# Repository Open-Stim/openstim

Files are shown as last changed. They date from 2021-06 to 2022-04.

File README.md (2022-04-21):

# <P align="center"> OPEN-STIM - OPEN SOURCE HARDWARE ARDUINO BASED ELECTRICAL STIMULATOR 
<table align='center'>
<tr align='center'>
<td align='center'>

Licence | OSHWA |
:-------------------------:|:-------------------------:|
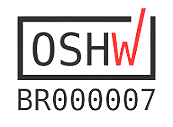
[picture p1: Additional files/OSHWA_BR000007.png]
(https://certification.oshwa.org/br000007.html)
 |  

</table> 
 
## <P align="center"> FEDERAL UNIVERSITY OF SÃO JOÃO DEL-REI – UFSJ
### <P align="center"> NEUROENGINEERING AND NEUROSCIENCE INTERDISCIPLINARY LABORATORY – LINNCE
&emsp; &emsp; &emsp; &emsp; &emsp; &emsp; &emsp; &emsp; &emsp; &emsp; &emsp; &emsp; &emsp;UFSJ &emsp; &emsp; &emsp; &emsp; LINNCE

### DEVELOPED BY:
Maikon Lorran Santos - maikon.lorran@hotmail.com <br/>
João Daniel Nolasco - joaodani@hotmail.com <br/>
Vinícius Rosa Cota: - vrcota@ufsj.edu.br <br/>

### PROJECT'S GOAL
<P align="justify"> The main objective of the project was to develop and build a low-cost electrical stimulator for experimental stimulation electrophysiology
based on the Arduino platform, maximizing ease of use, versatility, and openness. The idea was to develop an output stage shield capable of 
delivering mono or biphasic pulses with constant current (even in face of varying output impedances) easily attachable to an Arduino microcontroller
board. Stimulation parameters (pulse frequency, pulse duration, number and polarity of phases) can be controlled by a touch screen and/or by knobs.
In this entry, we published the version which is controlled mostly by a touch screen display, but this can be easily substituted by manual controls 
(switches and additional knobs) with or without a LCD display to further reduce costs (variation not yet published). These variations and openness of 
the design (which is provisionally certified by OSHWA with UID BR000007) makes Open Stim a very flexible stimulation platform for experienced users and, 
at the same time, also a ready-to-use device for researchers not skilled on electronics. 

### DISCLAIMER
<P align="justify"> We offer this design as is and although it has been successfully tested with care and to the best of our knowledge, we do not provide any 
 warranty in any aspect.

### STIMULATOR PARAMETERS
-Current: 15 µA up to 1200 µA <br/>
-Frequency: 0.1 Hz up to 300 Hz <br/>
-Duty Cycle: 4 µs up to 1 s <br/>
-Biphasic Pulses <br/>
-Low battery indicator <br/>

### OPEN STIM

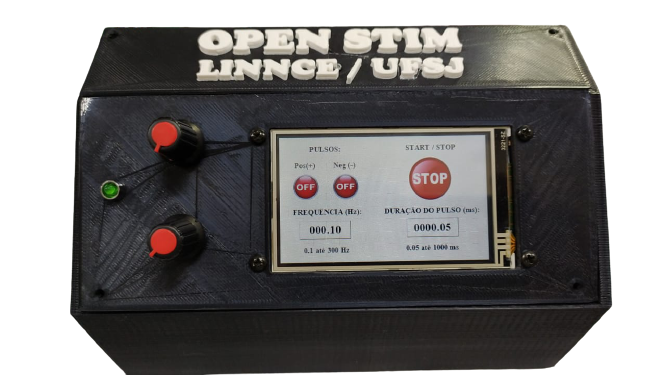
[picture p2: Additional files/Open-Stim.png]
OPEN-STIM

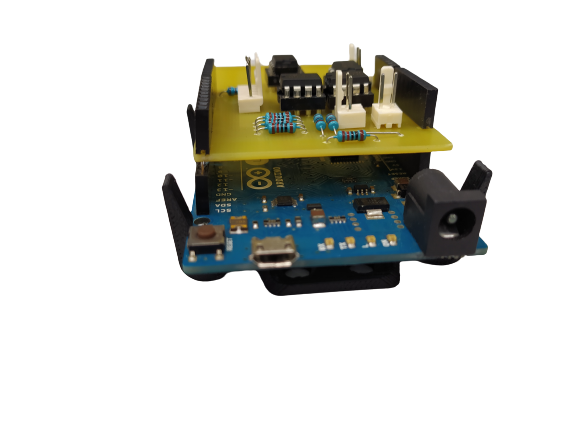
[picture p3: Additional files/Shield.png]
Shield
&emsp; &emsp; &emsp; 
### • More about the lab, at our website: [LINNce](https://ufsj.edu.br/vrcota/linnce.php)

### LICENSE
##### Documentation licensed under the Creative Commons Attribution Share Alike 4.0 International License

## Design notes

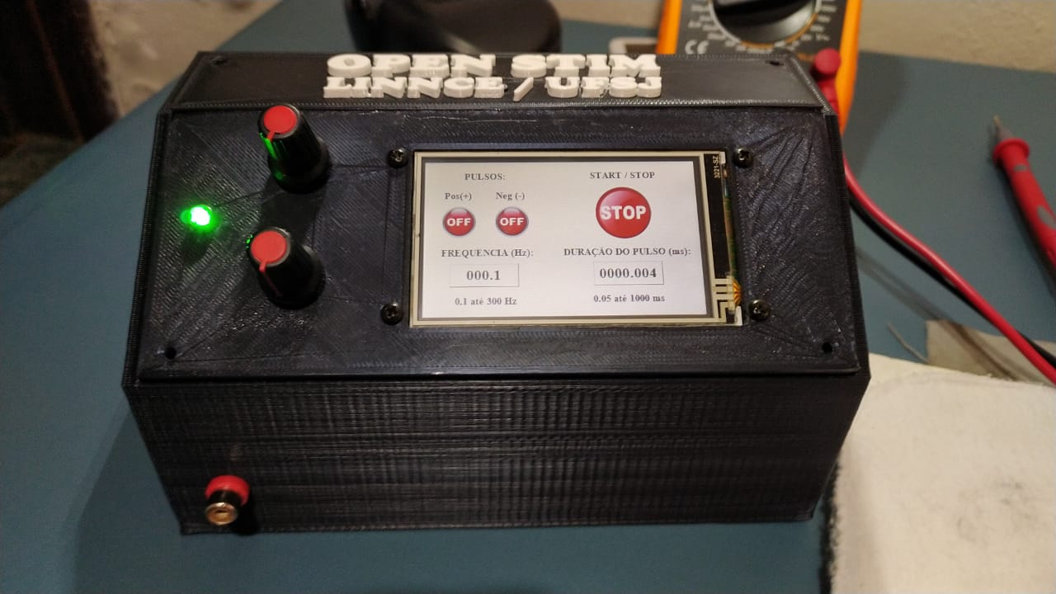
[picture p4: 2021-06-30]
Photos/Box/IMG-20210409-WA0050.jpg

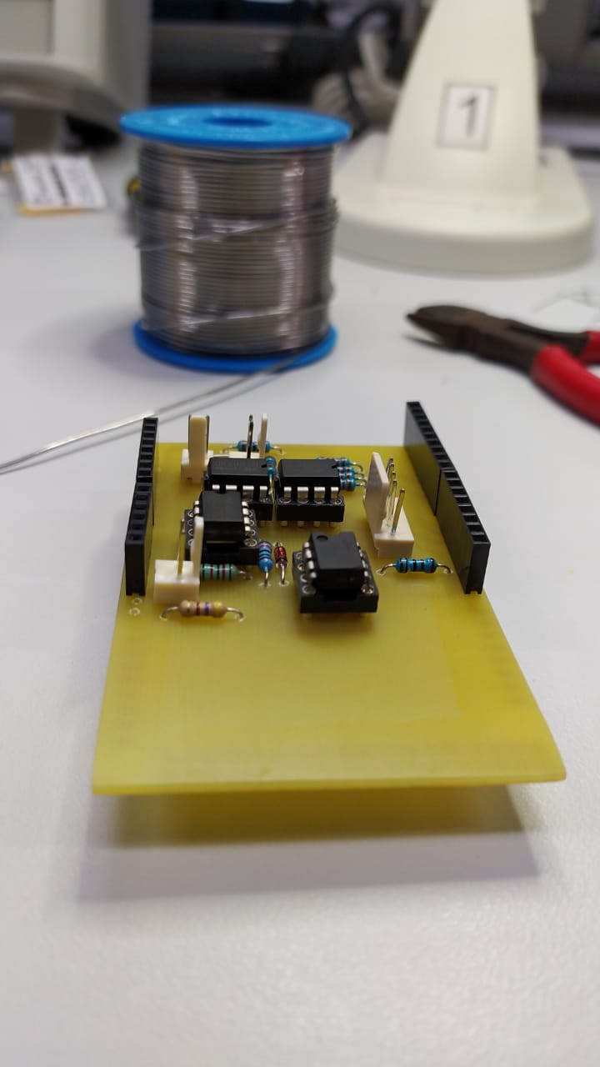
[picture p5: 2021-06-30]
Photos/PCB/Shield/IMG-20210302-WA0013.jpg

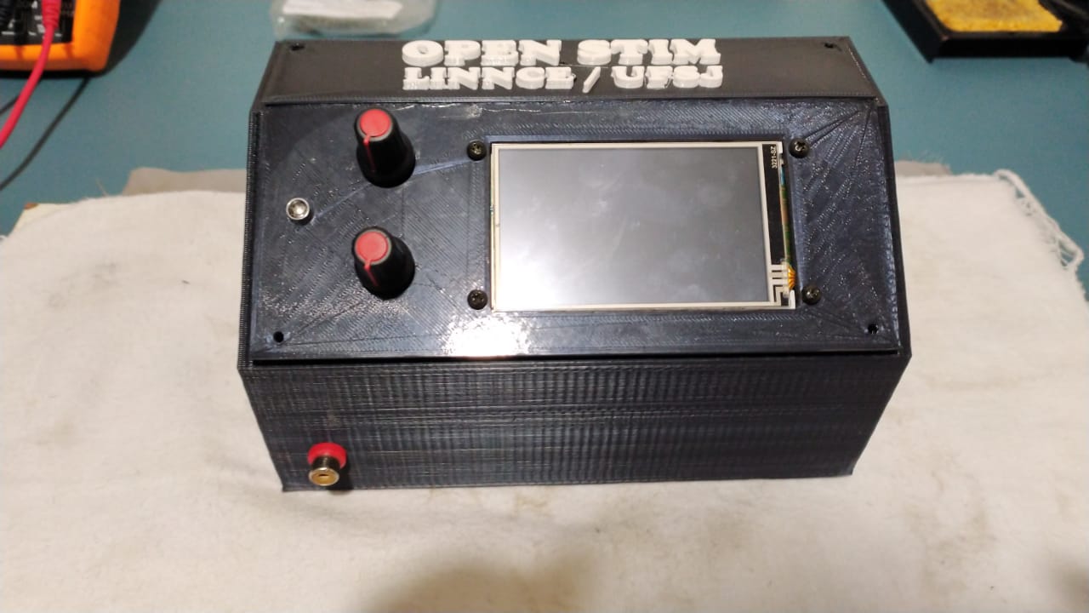
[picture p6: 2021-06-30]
Photos/Box/IMG-20210409-WA0058.jpg

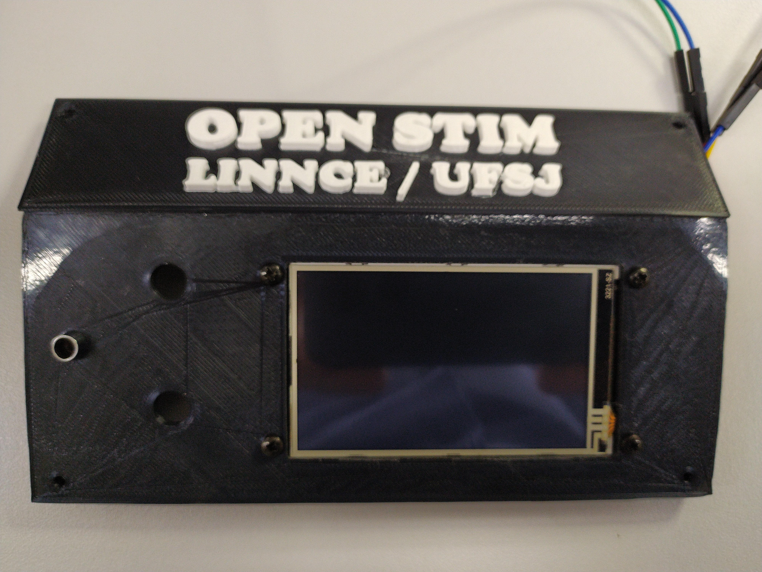
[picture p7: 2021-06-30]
Photos/Box/IMG_20210328_171714_BURST1.jpg

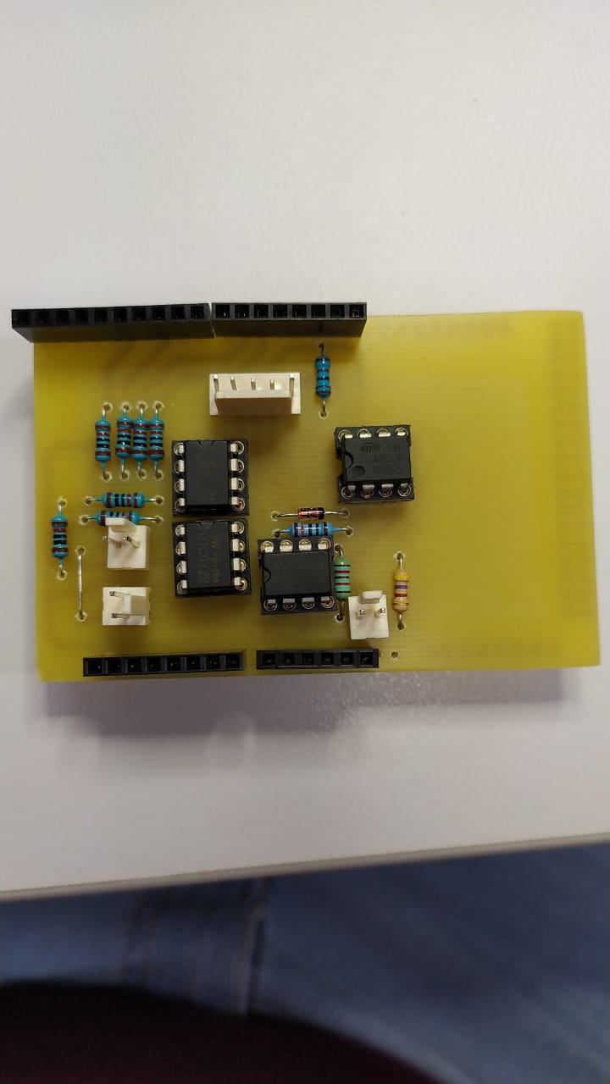
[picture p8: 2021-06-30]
Photos/PCB/Shield/IMG-20210302-WA0009.jpg

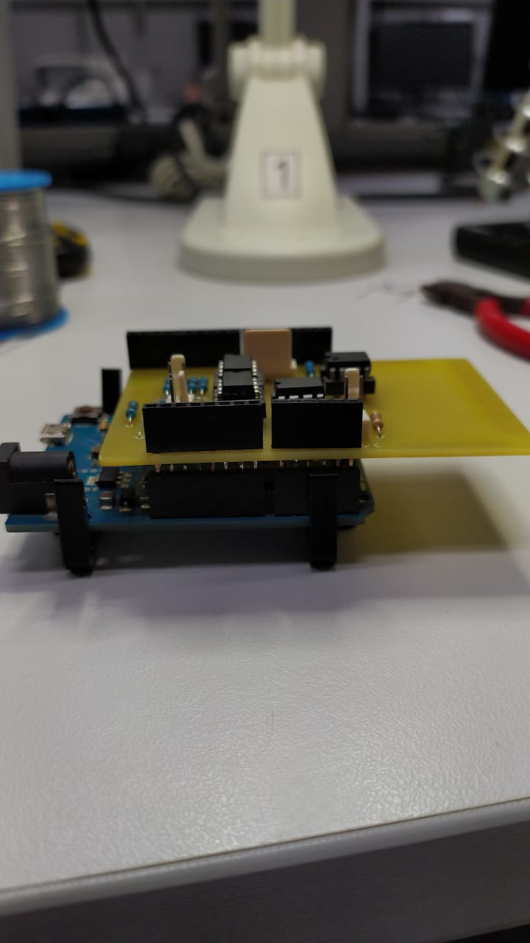
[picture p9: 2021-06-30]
Photos/PCB/Shield/IMG-20210302-WA0015.jpg

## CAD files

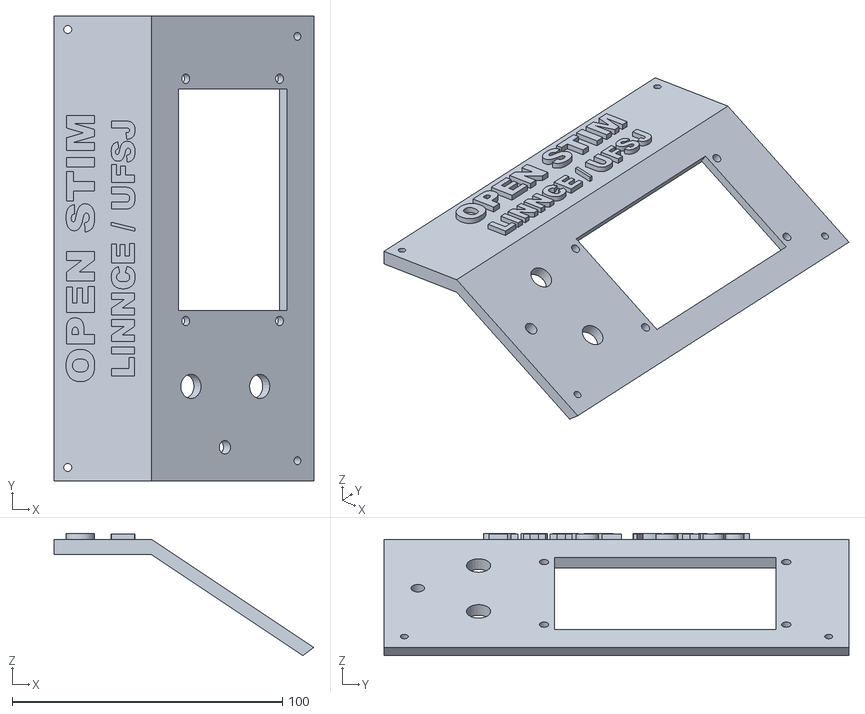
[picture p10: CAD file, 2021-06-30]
3D printing/SketchUp/STL print/Print_Cover.stl
96.0 x 172.0 x 45.2

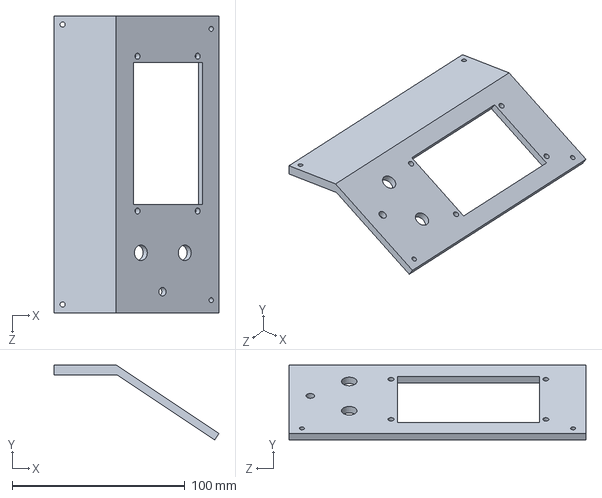
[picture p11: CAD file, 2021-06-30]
3D printing/SolidWorks/tampa.SLDPRT
95.5 x 43.4 x 171.8 mm

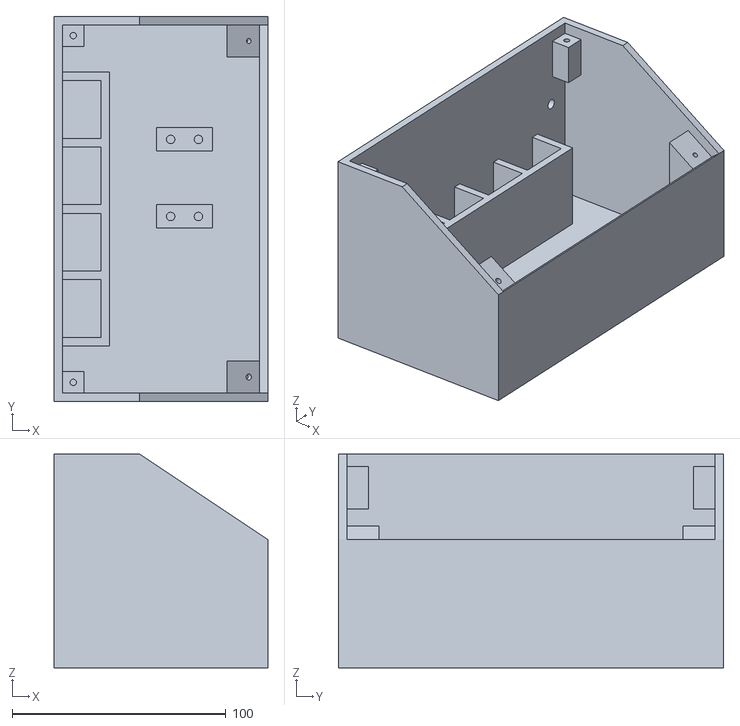
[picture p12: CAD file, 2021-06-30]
3D printing/SketchUp/STL print/Print_Box.stl
100.0 x 180.0 x 100.0

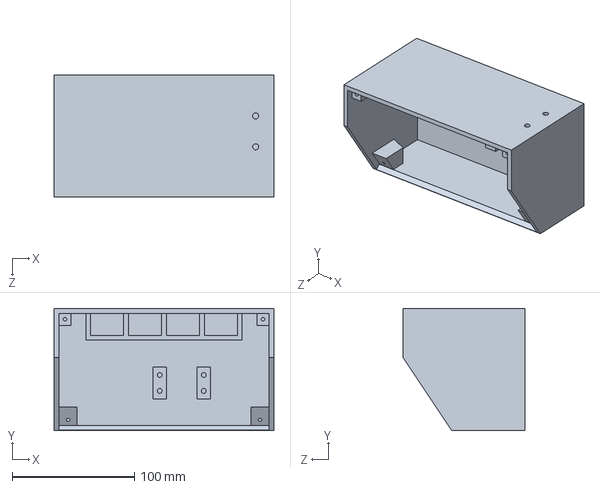
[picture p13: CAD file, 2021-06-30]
3D printing/SolidWorks/caixa.SLDPRT
180.0 x 100.0 x 100.0 mm

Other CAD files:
3D printing/SketchUp/Box Print/Box.skp
3D printing/SketchUp/Cover print/Cover.skp
3D printing/SolidWorks/caixa.IGS
3D printing/SolidWorks/tampa.IGS

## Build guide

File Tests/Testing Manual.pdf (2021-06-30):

OPEN STIM - ELECTRICAL STIMULATOR OPEN SOURCE HARDWARE

## FEDERAL UNIVERSITY OF SÃO JOÃO DEL-REI – UFSJ

NEUROENGINEERING AND NEUROSCIENCE INTERDISCIPLINARY LABORATORY – LINNCE

# OPEN STIM ELECTRICAL TESTING MANUAL

Brazil, May 2021

## OPEN STIM ELECTRICAL TESTING MANUAL

¹ FEDERAL UNIVERSITY OF SÃO JOÃO DEL-REI – UFSJ

² LABORATORY OF NEUROENGINEERING AND NEUROSCIENCE– LINNCE

DEVELOPED BY:

¹ ² Maikon Lorran Santos - maikon.lorran@hotmail.com

¹ João Daniel Nolasco - joaodani@hotmail.com

¹ ² Vinícius Rosa Cota: - vrcota@ufsj.edu.br

Address: Frei Orlando Square, 170, Center – São João del-Rei – Minas Gerais - Brazil

Brazil, May 2021

This manual will assist in testing Open

Stim. They are electrical tests, to be

carried out on bench with oscilloscope

and multimeter. It is possible to check the

frequency, the stimulation current, pulse

duration, pulse phase, slew rate, among

others.

## SUMMARY

3 | P á g i n a

# CHAPTER 1

## INTRODUCTION AND OBJECTIVES

The tests are of fundamental importance to verify all the functionalities and limitations

of the hardware and software. As it is a prototype, we do not have any tests performed on

animals yet. Thus, all the tests were carried out in an electronics laboratory, simulating the brain

or tissue with electrical resistors.

These tests enable us to verify that the configured parameters are actually being

delivered by the stimulator. In addition, we want to know the percentage of error contained in

each parameter, to establish its acceptable margins, and to find limitations. After all the tests

are done and results are consolidated and that the values found meet the need for your

research, there is the possibility of tests on animals. Bear in mind that, for tests on animals,

approval from the institution's ethics committee is required before starting any experimental

procedure.

The main purpose of this manual is explain how to check the frequency, pulse duration,

pulse phase, electrical current and slew rate being delivered by the stimulator.

# CHAPTER 2

## TESTING EQUIPMENT

To test Open Stim, we used the Agilent oscilloscope model DSO-X 2002A, which is shown

in Figure 1. However, any oscilloscope with basic functions is capable of carrying out the

necessary tests.

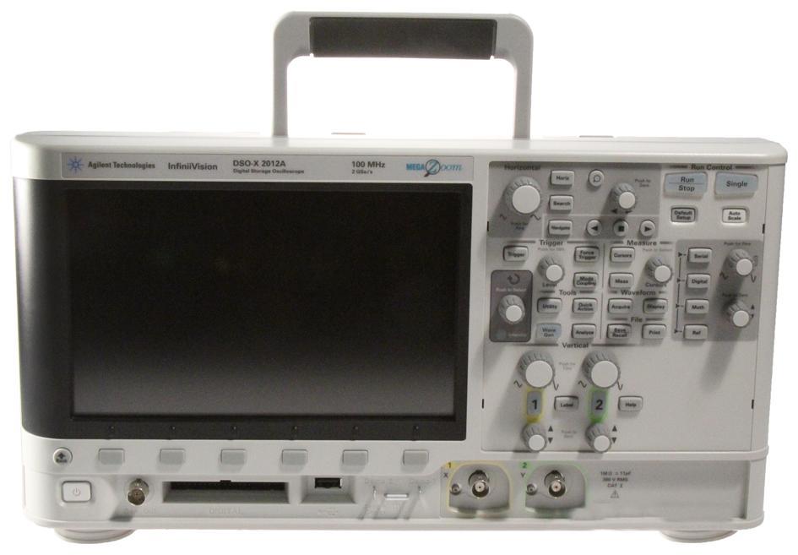
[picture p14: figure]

Figure 1 - Agilent DSO-X 2002A Oscilloscope

The multimeter used was the Agilent model U1241B, which is in Figure 2. It is important

that the multimeter is capable of measuring microamperes and has good accuracy, since the

stimulator supplies very low output currents. Before starting to measure the currents, check the

maximum current that the multimeter can measure, and also check that the low current fuse is

not open.

Another question that is a common mistake is the multimeter's probes. Check if they

are connected to the multimeter for current measurement. Also confirm the current scale to be

used, which is direct current in microamperes.

Finally, check the batteries of the multimeter, as it will be used for a long period of time.

Remove and measure all and, if necessary, replace them.

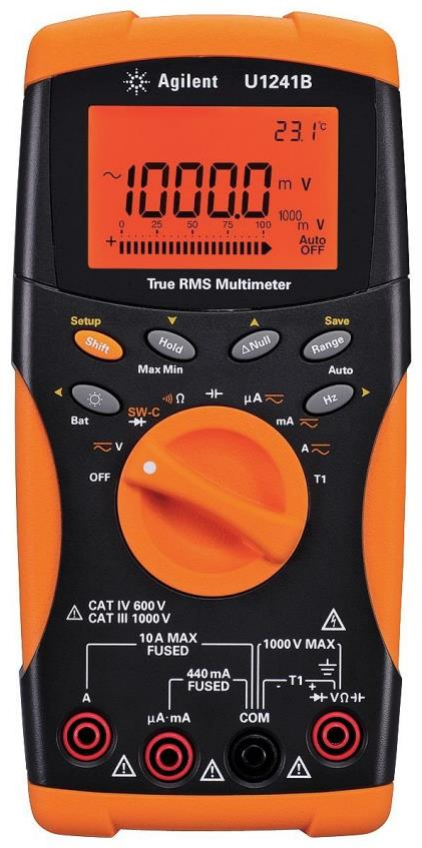
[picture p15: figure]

Figure 2 - Agilent U1241B Multimeter

We also recommend having on the bench some cables for jumpers, alligator claws,

cutting pliers, stripper pliers, electrical tape, note paper, pen, calculator, in short, everything

that will facilitate the quality of the tests.

# CHAPTER 3

## FREQUENCY TEST

To check the accuracy of the frequency, only the oscilloscope is needed. Consider 5 %

error for the frequency, this value meets the requirements of the project.

To carry out this test, put a resistance on the output, between 1K and 10K that will

simulate the brain of the animal. Place the ends of the oscilloscope in this output resistor. Now

turn on the stimulator, enter frequency values between 0.1 Hz and 300 Hz by typing the value

on to the Nextion screen. Of course, also entering the pulse width values is required, but at this

moment, we will not be checking this parameter, only the frequency. Enter large values of pulse

width, such as 50% of the duty cycle (period between firing of pulses), to facilitate viewing on the oscilloscope screen. For example: for a frequency of 20 Hz, the largest pulse width is 50 ms

However, as they are biphasic pulses, we have 25 ms for each pulse. Therefore, an average value

to be entered for pulse width for the frequency of 20 Hz would be 12.5 ms. Table 1 contains the

frequency results measured and the margin of error found for each value.

Table 1 - Frequency

If the frequencies are not within the expected levels, check the connections in order to

reduce or eliminate noise. Another point is to check the Arduino code, in case the difference is

very large, obtaining an error greater than 5%. Below are some screenshots of the oscilloscope,

showing the values found in the Open Stim built at UFSJ, by LINNCE.

FREQUENCY (Hz)

MEASURED

FREQUENCY (Hz)

ERROR (%)

300 | 299.19 | 0.27
250 | 249.60 | 0.16
200 | 199.63 | 0.18
150 | 149.78 | 0.15
100 | 99.95 | 0.05
90 | 89.92 | 0.09
80 | 79.85 | 0.19
70 | 69.86 | 0.20
60 | 59.84 | 0.26
50 | 49.93 | 0.14
40 | 39.99 | 0.02
30 | 29.96 | 0.13
20 | 19.94 | 0.30
15 | 14.96 | 0.27
10 | 9.99 | 0.1
9 | 8.99 | 0.11
8 | 7.99 | 0.12
7 | 6.98 | 0.29
6 | 5.99 | 0.17
5 | 4.99 | 0.20
4 | 3.99 | 0.25
3 | 2.99 | 0.33
2 | 1.99 | 0.50
1 | 0.99 | 1.0
0.5 | 0.48 | 4.17

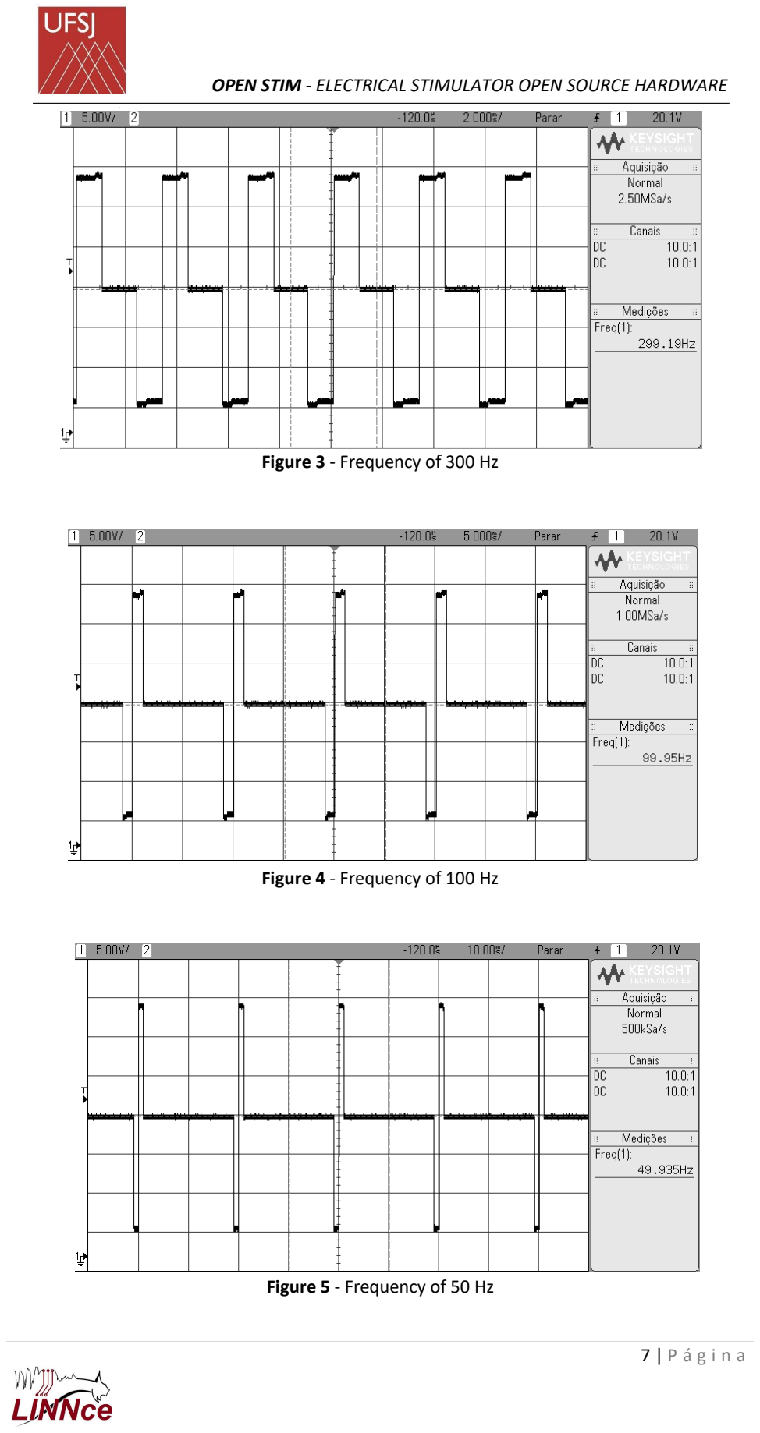
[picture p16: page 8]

Figure 3 - Frequency of 300 Hz

Figure 4 - Frequency of 100 Hz

Figure 5 - Frequency of 50 Hz

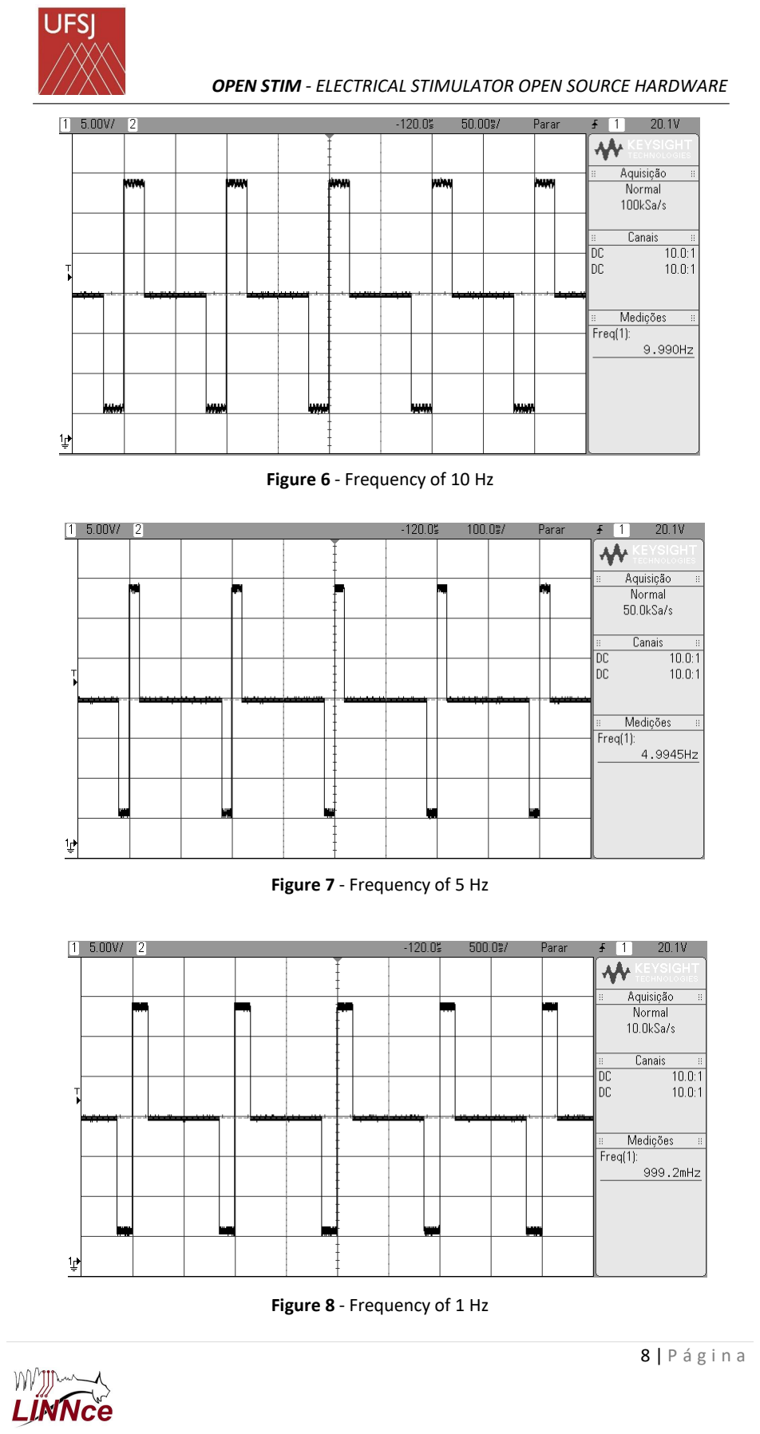
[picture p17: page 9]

Figure 6 - Frequency of 10 Hz

Figure 7 - Frequency of 5 Hz

Figure 8 - Frequency of 1 Hz

# CHAPTER 4

## PULSE WIDTH TEST

The pulse width test follows the same reasoning as the frequency test: enter the value

on the Nextion screen and check the value on the output with the oscilloscope and considering

a margin of error of 5 %. Table 2 shows some results found.

Table 2 - Pulse Width

The following screenshots show the values mentioned above. The values are found with

the aid of the oscilloscope cursor tool, over the X.

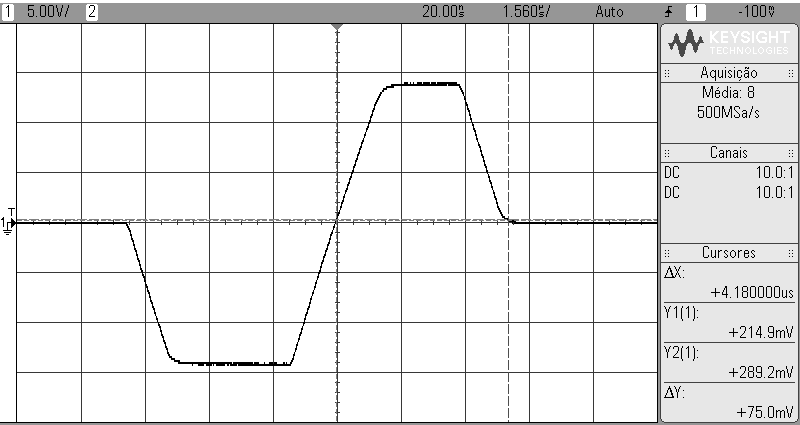
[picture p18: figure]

Figure 9 - Positive Pulse Width 4 µs

PULSE WIDTH (ms)

MEASURED POSITIVE

PULSE WIDTH (ms)

ERROR (%)

MEASURED NEGATIVE

PULSE WIDTH (ms)

ERROR (%)

4 µs (@280 Hz) | 4.18 µs | 4.31 % | 5.08 µs | 21.26 %
64 µs (@20Hz) | 64 µs | 0 % | 65.2 µs | 1.84 %
500 µs (@2 Hz) | 514 µs | 2.72 % | 514 µs | 2.72 %

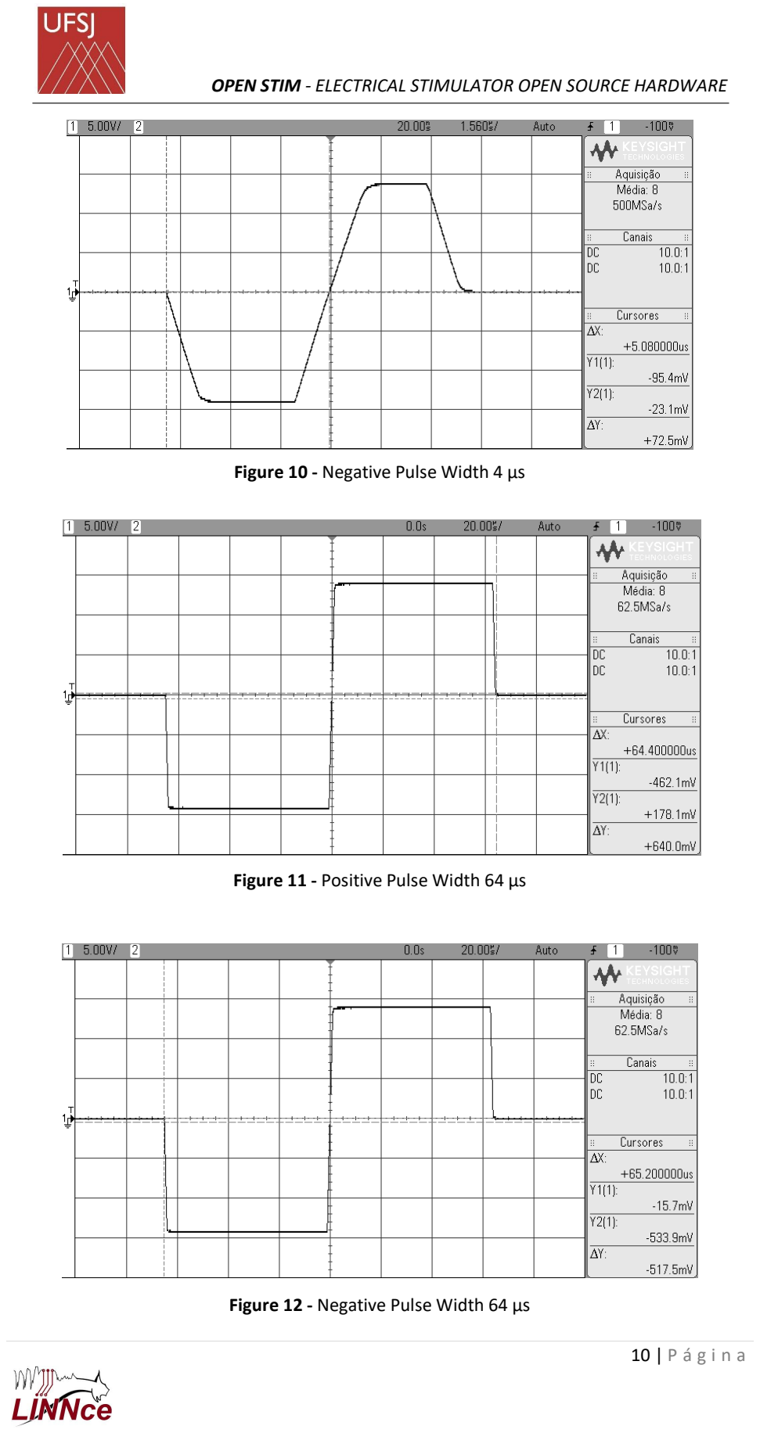
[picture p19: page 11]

Figure 10 - Negative Pulse Width 4 µs

Figure 11 - Positive Pulse Width 64 µs

Figure 12 - Negative Pulse Width 64 µs

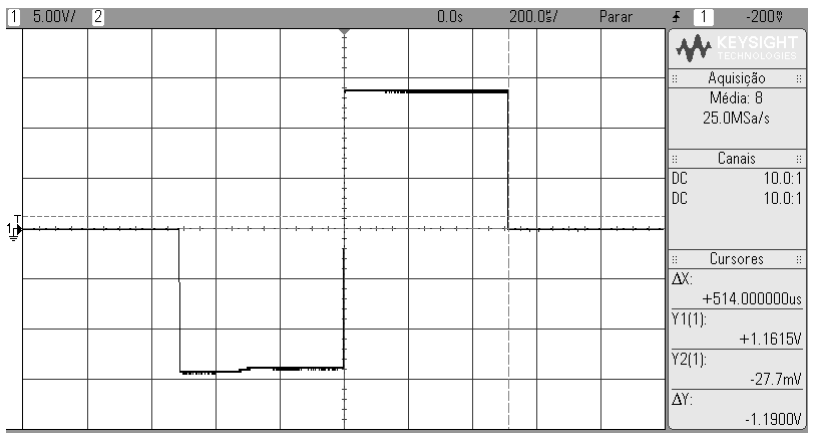
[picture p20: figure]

Figure 13- Positive Pulse Width 500 µs

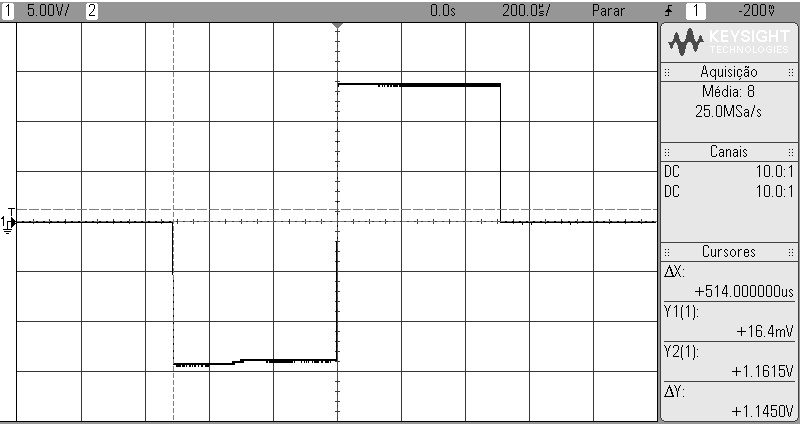
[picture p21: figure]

Figure 14 - Negative Pulse Width 500 µs

4.1 – PULSE WIDTH vs. FREQUENCY

As described in the Open Stim manual, the device is operated by means of PWM.

Thus, it depends solely on the 16 MHz internal clock of Atmega 32u4 processor. In this

sense, it is important to understand PWM operation and configuration in this processor

to fully grasp the link between these two parameters (pulse width and frequency), how

they interfere with each other, and what is the limitation of such form of operation.

When lower frequencies are desired, the frequency of the internal clock can be

divided by factors expressed as powers of base 2 (2N
) using the prescaler function (see

chapter 15 of the ATMEGA 32u4 datasheet). For instance, setting the prescaler to 1 yields the original frequency, that is, 16 MHz. When the prescaler is 2, we get 8 MHz,

and so on. Now, to obtain frequency values between the original frequency and its by-2

divisions, it is necessary to count a fixed quantity of clock pulses. This is done by the

internal Atmega 32u4 10-bit counter. Thus, for instance, if we use a prescaler of 64 and

a count of 1024 pulse, we obtain a frequency of 244.14 Hz.

250x10³
1024 = 244.14 Hz

Using the same prescaler, but counting 833 pulses instead, we get 300.12 Hz.

Table 3 below shows, according to the prescaler chosen, the new (divided) base

frequency, the minimum possible frequency (when 1024 pulses are counted), and the

maximum value of frequency used in this project (which is the minimum of the next

prescaler). We only show prescaler values used in our programming.

Configuration of pulse duration uses exactly the same clock system, including the

prescaler and the 10-bit counter. That means widths are limited to multiples of the pulse

duration of the divided clock signal. For instance, by using a prescaler value of 64, which

yields a divided frequency of 250 KHz, the minimum duration of a pulse will be 1/250000

Hz = 4 ms, which is shorter than most experimental applications in neuroscience. On the

other hand, if slower firing frequencies are desired, only longer pulse durations will be

available. For instance, if a prescaler of 16384 is used, the base frequency becomes

976,5625 Hz. In this case, the lowest frequency is circa 0.95 Hz with the shortest pulse

duration of 1.024 ms. Table 4 shows minimum pulse width obtainable for each prescaler.

In our experience, the range of values made available by this technology is

sufficient for a very wide range of experimental protocols used in neuroscience and also

in other areas of physiology (e.g., muscular and cardiac). If needed, one should consider

developing of a derivative of Open Stim using Arduino boards with better performance.

For instance, Arduino Due has an internal counter of 32 bits which will greatly improve

the granularity of pulse widths and frequency ranges. It is important to highlight, though,

that Arduino Due is not readily interchangeable with Leonardo, given, among other

technical aspects, differences in operation voltages (3.3 V vs. 5 V).

(1)

Table 3 - Frequency limits

Table 4 - Limit of pulse width by frequency range

For frequencies below 0.95 Hz, it is necessary to use the Arduino delay function and it is

no longer possible to do it directly using PWM. Using the delay function, the processor halts the

execution of the program until the commanded time has passed, which causes system

unresponsiveness. That is why such approach was avoided and used only when absolutely

necessary (frequencies below 0.95 Hz). Users and builders should bear this in mind when using

Open Stim or creating its derivatives.

PRESCALER | NEW FREQUENCY (Hz) | MINIMUM FREQUENCY (Hz) | MAXIMUM FREQUENCY (Hz)
64 | 250000 | 244.14 | 488.28
128 | 125000 | 122.07 | 244.14
256 | 62500 | 61.03 | 122.07
512 | 31250 | 30.52 | 61.03
1024 | 15625 | 15.26 | 30.52
2048 | 7812.5 | 7.63 | 15.26
4096 | 3906.25 | 3.81 | 7.63
8192 | 1953.125 | 1.91 | 3.81
16384 | 976.5625 | 0.95 | 1.91

PRESCALER

MINIMUM

FREQUENCY (Hz)

MAXIMUM

FREQUENCY (Hz)

MINIMUM PULSE

WIDTH (ms)

64 | 244.14 | 488.28 | 0.004
128 | 122.07 | 244.14 | 0.008
256 | 61.03 | 122.07 | 0.016
512 | 30.52 | 61.03 | 0.032
1024 | 15.26 | 30.52 | 0.064
2048 | 7.63 | 15.26 | 0.128
4096 | 3.81 | 7.63 | 0.256
8192 | 1.91 | 3.81 | 0.512
16384 | 0.95 | 1.91 | 1.024

# CHAPTER 5

## CONSTANT CURRENT TEST

The constant current test consists in verifying that output current stays the same

even if the output impedance changes, for instance, when performing stimulation to

different animals. Although simplistically, we can approximate the equivalent resistance

of Wistar rats’ brains to a range between 1 kΩ and 10 KΩ on average. Thus, we

performed the tests considering values between 1 KΩ and 10 KΩ, which were

represented by a resistor connected to the stimulator output.

With the multimeter connected in series with the output resistance and on the

direct current scale, proceed as follows:

1) Define the first value of output resistor with the first possible value being 1 KΩ and

the last possible value being 10 KΩ.

2) Define the resistor of the resistor board, that is, R10, the first possible value being

4.02 KΩ and the last 360 KΩ.

3) We suggest that you start as follows: Set the output resistance to 10 KΩ, which is the

maximum value, and vary R10 from 4.02 KΩ to 360 KΩ using the rotary switches. In this

way, all currents for output equal to 10 KΩ are measured. Note the positive and negative

current values. In order to obtain the correct current and not the average RMS, set a low

frequency with a large pulse width. In this way, the multimeter is able to make the

correct measurement. If you prefer, it is also possible to do it by assessing the voltage in

the output resistor and using Ohm's law relation to obtain the current.

4) After taking the measurements for R11 equal to 10 KΩ, change the resistance to a

lower one, in this work we use the following values: 1 KΩ, 2 KΩ, 4.02 KΩ, 6.12 KΩ, 7.15

KΩ, 8.25 KΩ and 10 KΩ. Follow in the same way as mentioned above and measure the

positive and negative currents to the value of 8.25 KΩ, for example. Then to 7.15 KΩ,

6.12 KΩ, 4.02 KΩ, 2 KΩ, 1 KΩ.

5) Now with all measured currents, calculate the error between the maximum and

minimum positive current and then the error between the maximum and minimum

negative current. This error cannot exceed 10%.

Table 5 and Table 6 show the positive and negative currents, respectively, with

the values found by the authors of the project, as well as their error.

Table 5 - Positive current measurement

R10 (KΩ) | 1 KΩ | 2 KΩ | 4,02 KΩ | 6,19 KΩ | 7,15 KΩ | 8,25 KΩ | 10 KΩ | ERROR
4,02 | 1252 | 1250 | 1247 | 1245 | 1244 | 1240 | 1239 | 1,04%
4,7 | 1068 | 1065 | 1064 | 1062 | 1061 | 1058 | 1050 | 1,69%
5,6 | 902 | 900 | 896 | 894 | 892 | 890 | 885 | 1,88%
6,19 | 810 | 806 | 805 | 804 | 803 | 800 | 795 | 1,85%
7,15 | 702 | 700 | 697 | 695 | 694 | 692 | 686 | 2,28%
8,25 | 609 | 606 | 605 | 604 | 604 | 600 | 595 | 2,30%
10 | 505 | 502 | 500 | 500 | 498 | 495 | 491 | 2,77%
12,1 | 415 | 414 | 413 | 413 | 411 | 405 | 400 | 3,61%
14 | 360 | 357 | 355 | 355 | 354 | 350 | 347 | 3,61%
16,9 | 302 | 300 | 298 | 295 | 294 | 291 | 288 | 4,64%
20,5 | 250 | 248 | 245 | 243 | 243 | 241 | 240 | 4,00%
24,9 | 208 | 206 | 205 | 202 | 199 | 197 | 195 | 6,25%
33,2 | 154 | 153 | 153 | 152 | 150 | 149 | 148 | 3,90%
44,2 | 115 | 114 | 112 | 110 | 111 | 110 | 108 | 6,09%
56,2 | 92 | 91 | 90 | 90 | 88 | 88 | 86 | 6,52%
61,9 | 83 | 83 | 82 | 81 | 80 | 79 | 77 | 7,23%
71,5 | 72 | 71 | 70 | 70 | 69 | 68 | 67 | 6,94%
78,7 | 64 | 64 | 63 | 63 | 62 | 62 | 61 | 4,69%
100 | 51 | 51 | 50 | 50 | 49 | 47 | 47 | 7,84%
120 | 43 | 42 | 42 | 41 | 41 | 40 | 39 | 9,30%
150 | 34 | 34 | 33 | 33 | 33 | 33 | 32 | 5,88%
240 | 22 | 22 | 22 | 21 | 21 | 21 | 20 | 9,09%
360 | 15 | 15 | 15 | 14 | 14 | 14 | 14 | 6,67%

Table 6 - Negative current measurement

# CHAPTER 6

## SLEW RATE

The Slew Rate is the rate of change of the output voltage over time, according to equation 6, with its unit of measurement V / µs.

SR =

dV0
dt

The slew rate of Open Stim is limited to the properties of the operational

amplifier, which cannot change its output voltage instantly when there is a change in

R10 (KΩ) | 1 KΩ | 2 KΩ | 4,02 KΩ | 6,19 KΩ | 7,15 KΩ | 8,25 KΩ | 10 KΩ | ERROR
4,02 | 1245 | 1241 | 1239 | 1238 | 1238 | 1238 | 1235 | 0,80%
4,7 | 1059 | 1059 | 1057 | 1055 | 1055 | 1054 | 1048 | 1,04%
5,6 | 897 | 895 | 892 | 890 | 890 | 888 | 885 | 1,34%
6,19 | 807 | 805 | 803 | 802 | 800 | 799 | 795 | 1,49%
7,15 | 695 | 694 | 692 | 691 | 690 | 687 | 685 | 1,44%
8,25 | 605 | 604 | 603 | 602 | 601 | 599 | 596 | 1,49%
10 | 500 | 498 | 496 | 495 | 495 | 493 | 490 | 2,00%
12,1 | 413 | 411 | 410 | 408 | 408 | 405 | 400 | 3,15%
14 | 357 | 355 | 354 | 353 | 352 | 350 | 345 | 3,36%
16,9 | 300 | 297 | 295 | 293 | 292 | 291 | 290 | 3,33%
20,5 | 247 | 245 | 244 | 242 | 242 | 240 | 238 | 3,64%
24,9 | 205 | 202 | 200 | 199 | 198 | 197 | 195 | 4,88%
33,2 | 152 | 150 | 149 | 149 | 149 | 147 | 145 | 4,61%
44,2 | 115 | 114 | 112 | 112 | 111 | 110 | 108 | 6,09%
56,2 | 91 | 91 | 90 | 88 | 87 | 87 | 85 | 6,59%
61,9 | 82 | 81 | 80 | 80 | 79 | 79 | 77 | 6,10%
71,5 | 72 | 71 | 70 | 70 | 69 | 68 | 67 | 6,94%
78,7 | 64 | 64 | 63 | 62 | 62 | 61 | 60 | 6,25%
100 | 51 | 50 | 50 | 49 | 49 | 48 | 48 | 5,88%
120 | 42 | 42 | 41 | 41 | 40 | 39 | 39 | 7,14%
150 | 34 | 34 | 34 | 33 | 33 | 32 | 31 | 8,82%
240 | 22 | 22 | 21 | 21 | 20 | 20 | 20 | 9,09%
360 | 14 | 14 | 14 | 13 | 13 | 13 | 13 | 7,14%

(2)

the input voltage, as shown in Figure 15. Therefore, if the input signal is to demand a

response at the output with a rate greater than the value specified in the slew rate, the

amplifier will not respond as expected.

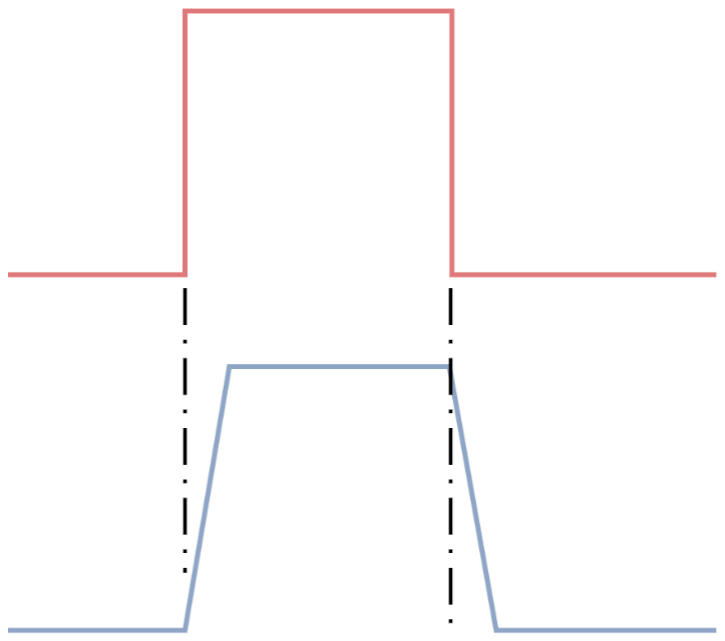
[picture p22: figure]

Figure 15 - Slew Rate: Response of the output signal in relation to the input

Ideally, to measure the slew rate, we take the interval between 10% and 90% of

the signal change curve. That is, we disregard the first 10% and the last 10% to avoid

noise fluctuations and curving of baseline that could impair reading. Figure 16 shows

how it is done.

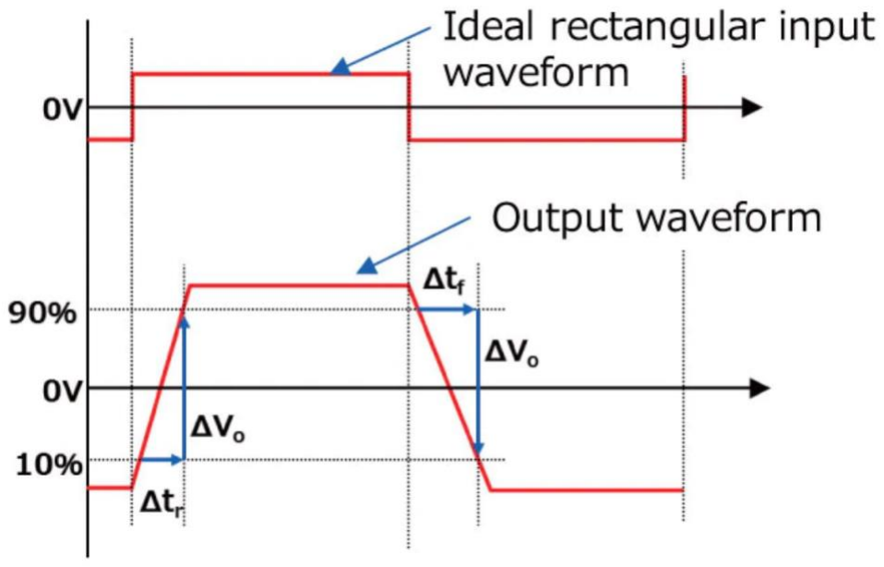
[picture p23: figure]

Figure 16 - Slew Rate: measurement between 10% and 90% of the

characteristic curve to obtain Δt e ΔV0

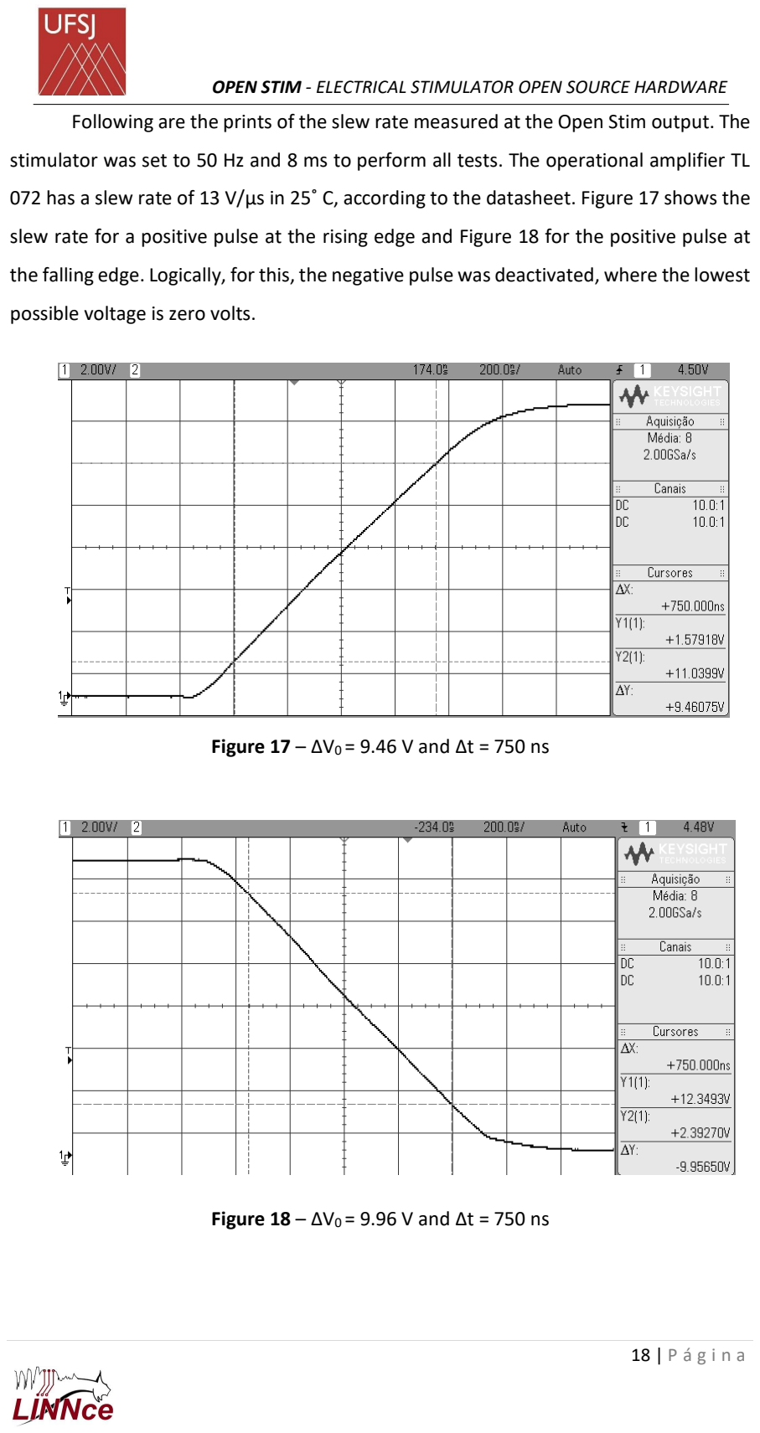
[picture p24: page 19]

Following are the prints of the slew rate measured at the Open Stim output. The

stimulator was set to 50 Hz and 8 ms to perform all tests. The operational amplifier TL

072 has a slew rate of 13 V/µs in 25˚ C, according to the datasheet. Figure 17 shows the

slew rate for a positive pulse at the rising edge and Figure 18 for the positive pulse at

the falling edge. Logically, for this, the negative pulse was deactivated, where the lowest

possible voltage is zero volts.

Figure 17 – ΔV0 = 9.46 V and Δt = 750 ns

Figure 18 – ΔV0 = 9.96 V and Δt = 750 ns

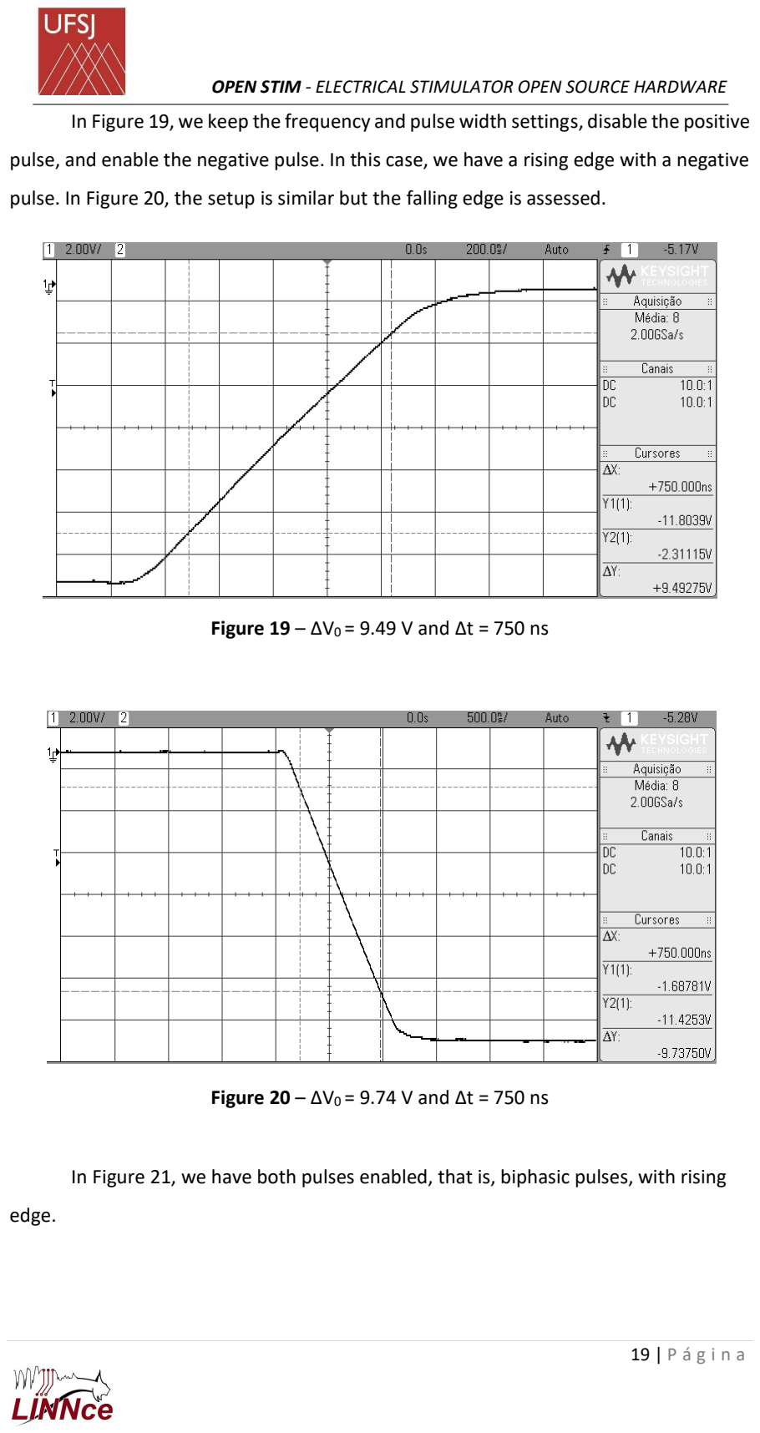
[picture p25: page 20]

In Figure 19, we keep the frequency and pulse width settings, disable the positive

pulse, and enable the negative pulse. In this case, we have a rising edge with a negative

pulse. In Figure 20, the setup is similar but the falling edge is assessed.

Figure 19 – ΔV0 = 9.49 V and Δt = 750 ns

Figure 20 – ΔV0 = 9.74 V and Δt = 750 ns

In Figure 21, we have both pulses enabled, that is, biphasic pulses, with rising

edge.

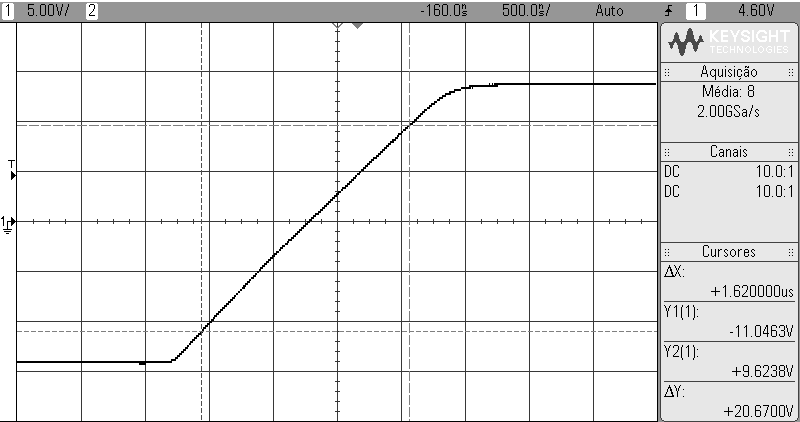
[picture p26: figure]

Figure 21 – ΔV0 = 20.67 V and Δt = 1.62 µs

For each Figure, we calculate the slew rate found, remembering that the unit of

measurement is V/µs.

To Figure 17:

SR =

9.46
750000 = 12.61 V/μs

To Figure 18:

SR =

9.96
750000 = 13.28 V/μs

To Figure 19:

SR =

9.49
750000 = 12.65 V/μs

To Figure 20:

SR =

9.74
750000 = 12.99 V/μs

To Figure 21:

SR =

20.67
1.62 = 12.76 V/μs

(3)

(4)

(5)

(6)

(7)

Values obtained are, as expected, very close to those described in the operational

amplifier (TL072) datasheet. It noteworthy that the chosen IC, in addition to having low

noise, presents a great slew rate, in face of its low cost (e.g., nominal slew rate of LM741

is only 0.5 V/ s slew rate, although costs are similar). If faster output are needed, one

should consider interchanging the IC for superior models, while considering the impact

on costs.

# CHAPTER 7

## DEAD TIME

As we have already seen in the case of the slew rate, we also have dead time,

this delay essentially depends on the distance between the points and the speed with

which the transfer is made. The shorter the distance between the points, the shorter

the delay time, the higher the transfer speed, the shorter the dead time. In other words,

the dead time, is the time interval between the instant when the system undergoes any

variation and the instant when it begins to respond to that variation.

To start analyzing the dead time on the Open Stim circuit, we look at Figure 22,

which presents an example of dead time on any system.

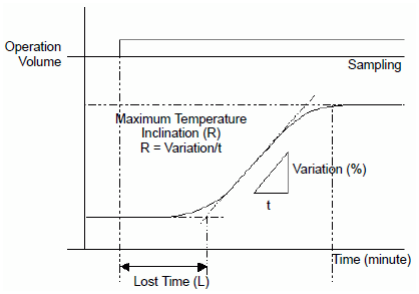
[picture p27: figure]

Figure 22 - Example of dead time

In Figure 23, we have a positive and negative pulse (anodic and cathodic),

however, without the necessary zoom to see in detail the slew rate or dead time. In

Figure 24 we have a zoom of Figure 23, where it is already possible to notice that there

is a slew rate, as shown in the previous chapter, but we still don't notice dead time.

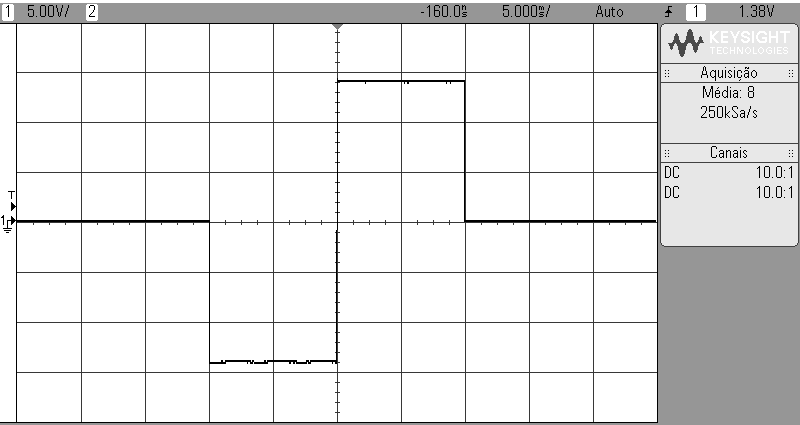
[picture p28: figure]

Figure 23 - Positive and negative pulse (anodic and cathodic)

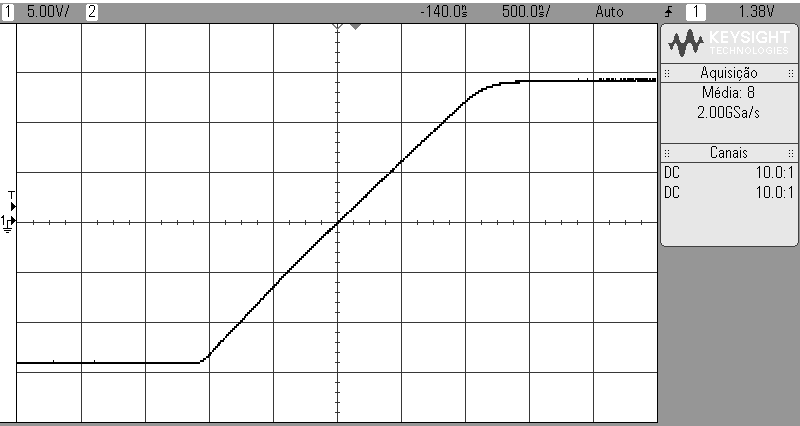
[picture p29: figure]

Figure 24 - Positive and negative pulse (anodic and cathodic) – Zoom of the positive pulse

In Figure 25, the zoom has been enlarged even further, and here it is already

possible to say that the dead time of the circuit is very close to zero. This is probably due

to the choice of using Arduino’s PWM function to generate the pulses.

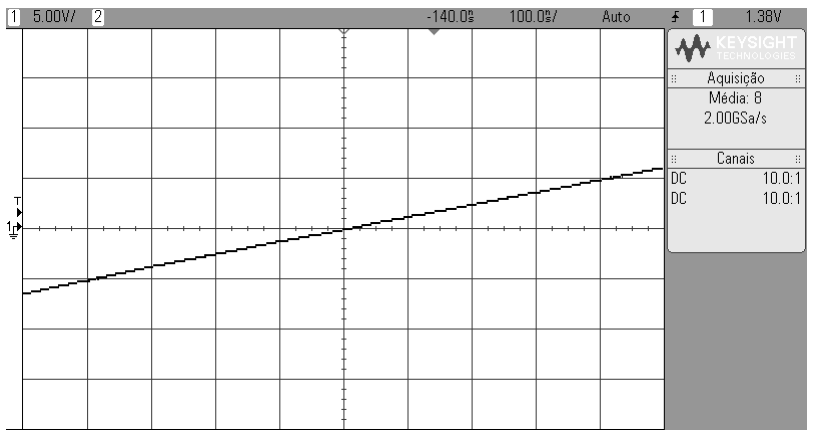
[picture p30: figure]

Figure 25 - Magnified zoom of the positive pulse: dead time is zero

# FINAL CONSIDERATIONS

The Laboratory of Neuroengineering and Neuroscience - LINNce of the Federal

University of São João del-Rei - UFSJ, hopes that, with this equipment and with all the tests

carried out, you can start or continue your research inside or outside a university or technical

school.

If, during the tests, the stimulator shows any non-standard results, first check the cables,

solders and batteries, and then change the components. If the problem is still not resolved,

return to the assembly manual. If you encounter any limitations or technical mistakes in our

design, testing, and application, please let us know by discussing it in the repository forum. This

will help us develop a more robust and safer tool for electrophysiological experiments.

We appreciate your interest in getting to know our stimulator and we count on your

contributions to improve the project through GitHub. See you soon and good studies!

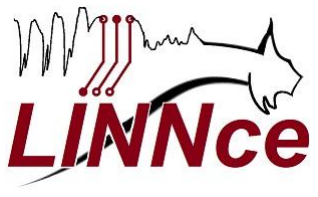
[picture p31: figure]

# ACKNOWLEDGMENTS

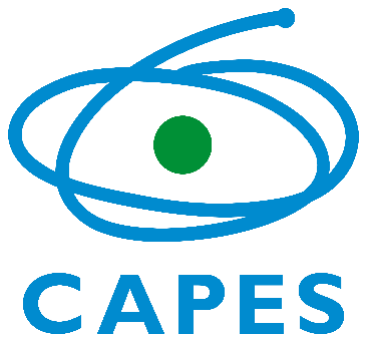
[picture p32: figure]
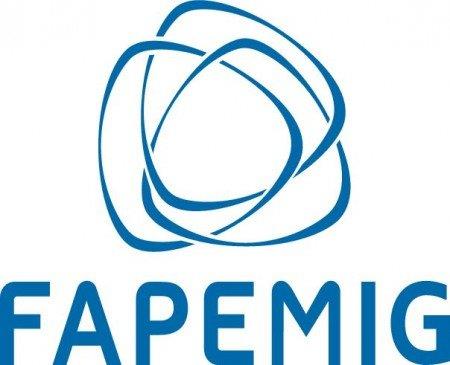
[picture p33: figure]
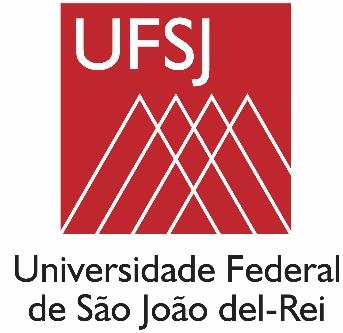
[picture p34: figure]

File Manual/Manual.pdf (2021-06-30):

## FEDERAL UNIVERSITY OF SÃO JOÃO DEL-REI – UFSJ

LABORATORY OF NEUROENGINEERING AND NEUROSCIENCE – LINNCE

# OPEN-STIM

# OPEN SOURCE HARWARE ARDUINO BASED ELECTRICAL STIMULATOR

# ASSEMBLY INSTRUCTION MANUAL

Brazil, May 2021

## OPEN SOURCE HARWARE STIMULATOR

## ASSEMBLY INSTRUCTION MANUAL

¹ FEDERAL UNIVERSITY OF SÃO JOÃO DEL-REI – UFSJ

² NEUROENGINEERING AND NEUROSCIENCE INTERDISCIPLINARY LABORATORY – LINNCE

DEVELOPED BY:

¹ ² Maikon Lorran Santos - maikon.lorran@hotmail.com

¹ João Daniel Nolasco - joaodani@hotmail.com

¹ ² Vinícius Rosa Cota: - vrcota@ufsj.edu.br

Address: Pça. Frei Orlando, 170, Centro – São João del-Rei – Minas Gerais - Brazil

Brazil, May 2021

This manual will assist builders in the

construction and assembly of the Open

Source Hardware Electrical Stimulator. All

steps are described in detail, showing the

diagrams, PCB, simulation, codes, and

photos.

### SUMMARY

3 | P á g i n a

OPEN STIM - ELECTRICAL STIMULATOR OPEN SOURCE HARDWARE

# CHAPTER 1

## DESCRIPTION OF MAIN GOALS

The main objective of the project is to develop and build a low-cost electrical stimulator

for experimental electrophysiology based on the Arduino platform. The idea is to build a Shield

capable of controlling the output current and keeping it constant even if the load changes, that

is, independent of the animal/tissue being stimulated and possible changes of impedance.

In the stimulator configuration, it is possible to vary the frequency, the pulse width, the

pulse phase, that is, positive, negative or both and of course, the current. Current amplitude is

configured by two wave switches, also known as the rotary switches For frequency, pulse width

and pulse phase, the Nextion display will be used, which is a Touch Screen that has its own

processor and its own programming language, but which communicates very well with several

platforms, being one of most used, the Arduino.

The entire stimulator is powered by four 9 V batteries. These batteries are monitored

by an exclusive circuit, which indicates when it is necessary to change or recharge them.

The entire project is built with precision resistors, with error less than or equal to 1%.

To accommodate the boards and display, a custom box is built with 3D printing. We highlight

that all software used in developing this project have free or student licenses, which do not

prevent or compromise the construction of the stimulator or modification of the design.

The project has a CC BY-SA 4.0 license which is accepted by the Open Source Hardware

Association (OSHWA); the details of this license can be found in the next chapter.

Finally, with this project, it is expected that:

1) Laboratories from any part of the world can have a stimulator due to its easy and low-cost

construction. Standard stimulation protocols (e.g. fixed frequency) is promptly available. Yet,

once it is customizable, users can implement their own protocols by changing control software.

2) The design is able to raise the interest of students, academics or even lay people (hobbyists)

in the subject of electrical stimulation as a powerful investigational tool and as a means for the

treatment of chronic disorders. In this way, we will have more thinking heads devoting

themselves to the same important objective.

3) That the stimulator design is improved by qualified and extensive peer review. We want it to

have more versions, with its hardware and software improved.

4) Let it be a way of including people in the doing of science. With such a simple and inexpensive

design, we believe that even in a school it will be possible to build and teach something about electronics, programming, 3D printing. In short, it is possible to do science without high cost and

include and encourage more people in favor of science.

Given the above, we would like to present the world, OPEN STIM!

# CHAPTER 2

## SPECIFICATIONS

### 2.1 GENERAL SPECIFICATIONS:

The stimulator has the following specifications in its current version (1.0):

- Electric Current: from 15 µA to 1200 µA
- Frequency: from 0.1 Hz to 300 Hz
- Pulse Duration: from 4µs to 1000ms
- Pulses polarity: positive and negative (cathodic or anodic, depending on wiring)

### 2.2 WEB SITE:

The entire project is hosted on GitHub. You can access it using the link:

### https://github.com/Open-Stim/openstim

In the above GitHub directory, it is possible to have complete access to the files, such

as: Shield PCB, diagrams, simulations, Arduino codes and Nextion display, STL files for 3D

printing, in addition to the photos of each construction and assembly step.

### 2.3 LICENCE:

The project is distributed under the Creative Commons BY-SA 4.0 license. With this

license you will be able to:

Share - copy and redistribute material in any medium or format

Adapt - remix, transform, and create from the material for any purpose, even commercial.

According to the CC BY-AS 4.0 (https://creativecommons.org/licenses/by-sa/4.0/deed.en) the terms are:

ATTRIBUTION - You must give appropriate credit, provide a link to the license,

and indicate if changes were made. You may do so in any reasonable manner, but

not in any way that suggests the licensor endorses you or your use.

SHAREALIKE - If you remix, transform, or build upon the material, you must distribute your contributions under the same license as the original.

### 2.4 ARDUINO LEONARDO

The choice for this project was the Arduino Leonardo, due to its low cost and

compatibility with the project specifications. The documentation for the arduino Leonardo can

be found at: https://www.arduino.cc/en/Main/Arduino_BoardLeonardo. Figure 1 shows the

Arduino Leonardo board.

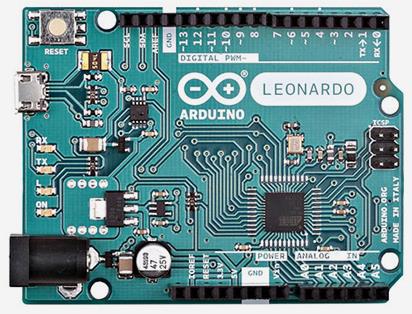
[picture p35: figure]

Figure 1 – Arduino Leonardo

Some of the specifications of the Leonardo Arduino are:

Microcontroller | ATmega32u4
Operating Voltage | 5V
Input Voltage (Recommended) 7-12V
Input Voltage (limits) | 6-20V
Digital I/O Pins | 20
PWM Channels | 7
Analog Input Channels | 12
DC Current per I/O Pin | 40 mA
DC Current for 3.3V Pin | 50 mA
Flash Memory | 32 KB (ATmega32u4) of which 4 KB used by bootloader
SRAM | 2.5 KB (ATmega32u4)
EEPROM | 1 KB (ATmega32u4)
Clock Speed | 16 MHz
Length | 68.6 mm
Width | 53.3 mm
Weight | 20 g

The complete documentation for the Atmel 32u4 processor can be found at: https://ww1.microchip.com/downloads/en/DeviceDoc/Atmel-7766-8-bit-AVR-ATmega16U4-32U4_Datasheet.pdf (https://ww1.microchip.com/downloads/en/DeviceDoc/Atmel-7766-8-bit-AVR-ATmega16U4-32U4_Datasheet.pdf)

### 2.5 NEXTION DISPLAY

The tft display chosen was the Nextion 3.2 "model NX4024T032. It is among the most

basic models available, and of course has a lower cost. It has a resolution of 400 x 240 Pixels,

RAM memory of 3584 bytes, Flash memory of 4 MB, screen resistive touch, 5 V power supply,

requiring 85 mA (at maximum brightness) and 15 mA (at minimum brightness). Additionally, it

has an input for a microSD memory card of up to 32 GB formatted in Fat32. Figure 2 shows the

Nextion display used.

Figure 2 – Display Nextion 3.2”- NX4024T032

The manufacturer's official website is: https://nextion.tech/ and the datasheet of the

model in question can be accessed at: https://nextion.tech/datasheets/nx4024t032/

As it can be seen in Figure 2, only 4 connections are required for the display to work,

namely: 5V and GND for power and RX and TX for communication with Arduino.

### 2.6 OPERATIONAL AMPLIFIERS

Only two operational amplifiers are used: TL072 and LM741. The choice of TL072 is due

to its low noise and it is responsible for the main part of the project, generating pulses at the

output. The LM741 is chosen for its low cost and will be responsible for monitoring the batteries,

indicating the time for changing or recharging. The TL072 and LM741 datasheet can be accessed

through the links below:

TL072: https://pdf1.alldatasheet.com/datasheet-pdf/view/28775/TI/TL072.html

LM741: https://pdf1.alldatasheet.com/datasheet-pdf/view/66375/INTERSIL/LM741.html

Figure 3 shows the TL072 operational applier and Figure 4 the LM741 operational

amplifier. The connection of the TL072 pins is shown in Figure 5 and the LM741 in Figure 6.

Figure 3 – TL072 | Figure 4 – LM741

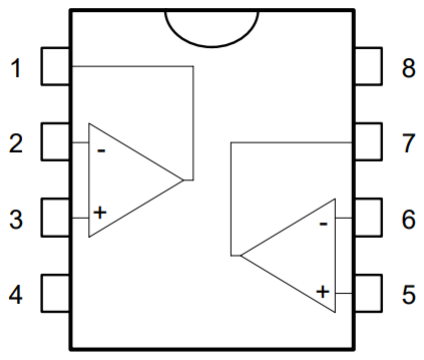
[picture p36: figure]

Figure 5 – Connection pins TL072

Figure 6 – Connection pins LM741

1 - Offset null 1
2 - Inverting input 1
3 - Non-inverting input 1
4 - (-) VCC
5 - Non-inverting input 2
6 - Inverting input 2
7 - Output 2
8 - (+) VCC

1 - Offset null
2 - Inverting input
3 - Non-inverting input
4 - (-) VCC
5 - Non-inverting input 2
6 - Output
7 - (+) VCC
8 - NC

# CHAPTER 3

## DIAGRAM AND SIMULATION

3.1 – DIAGRAM CONSTANT CURRENT CIRCUIT

The software used for simulation is LT Spice, which can be downloaded through the link: https://www.analog.com/en/design-center/design-tools-and-calculators/ltspice-simulator.html# (https://www.analog.com/en/design-center/design-tools-and-calculators/ltspice-simulator.html) (available to Windows and Mac).

Figure 7 shows the Open Stim diagram. Next, the circuit's operation will be detailed.

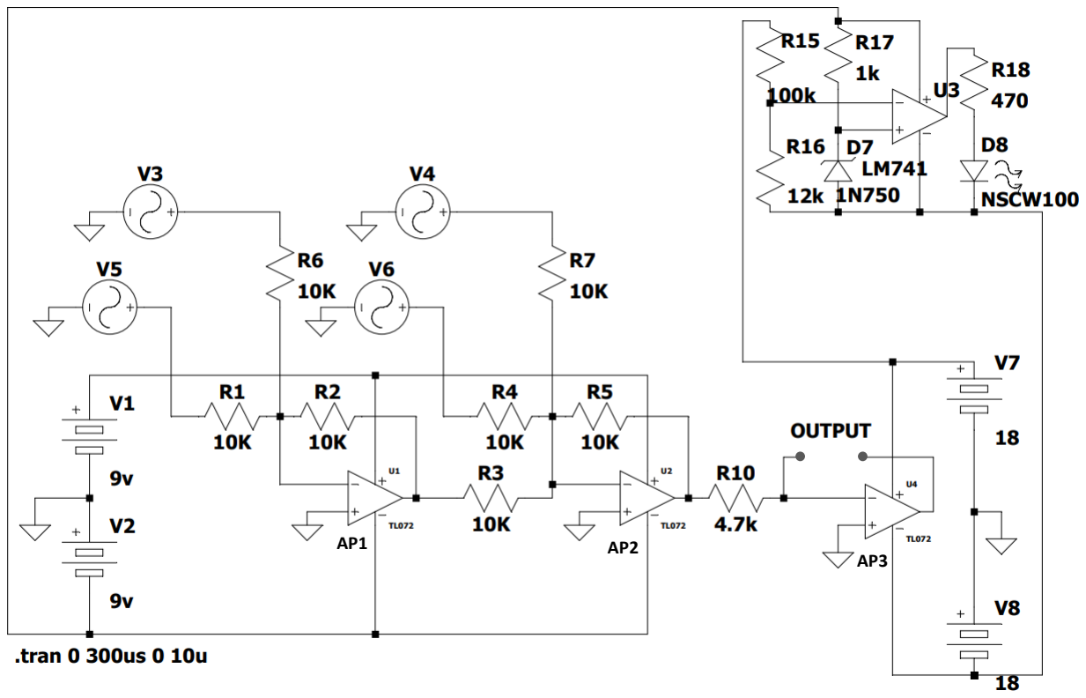
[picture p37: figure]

Figure 7 - Electronic Diagram

We started the analysis with the first operational amplifier represented by AP1 (TL072)

connected in the configuration of the adder with the voltages of V3 and V5, which has its

connection according to Equation 1. As there is no amplification because all the resistors of R1a

R7 are all the same at 10 KΩ, we can cancel, and simplify the Vout1 equation.

The voltage output Vout1 is the input of the second operational amplifier (AP2) together

with V4 and V6, and therefore, all will be added together. Following the same analogy as

Equation 1, we have Vout2 in Equation 2. Simplifying again due to the equal resistors, we come

to Equation 3. Equation 4 is just the algebraic manipulation of Equation 3.

Therefore, we have to: V5 and V6 generate the main waves, and V3 and V4 cut the main

waves so that the desired pulse widths are obtained. So, we have V5 being cut by V4 and V6 being cut by V3. Without the 4 waves, it would be impossible with a certain fixed frequency to

vary the pulse width. Another consideration is that the negative wave is generated in the first

stage, that is, in AP1 and the positive wave in the second stage, in AP2.

Vout1 = − (

R2
R1

V5 +

R2
R6

V3) = −(V3 + V5)

Vout2 = − (

R5
R3

Vout1 +

R5
R4

V6 +

R5
R7

V4) = −(−(V3 + V5) + V4 + V6)

Vout2 = ((V3 + V5) − V4 − V6)

Vout2 = (V5 − V4) − (V6 − V3)

In the Arduino, the pins 6 and 10 generate the negative pulse, while pins 5 and 12

generate the positive pulse. Pins 5 and 6 are the main waves and the waves from pins 10 and 12

are responsible for cutting the main waves.

The AP3 (TL072) amplifier receives the signal according to the configuration made by

the user in relation to the number and polarity of phases, frequency and duration of the pulse.

It is connected as a voltage-current converter. Resistor R10 controls the current and is actually

the resistor board containing 23 resistors, ranging from 4.02 KΩ to 360 KΩ that translates to a

current between 15 µA to 1200 µA. As previously mentioned, the signal received by AP3 is at

the inverter port, therefore, the signal will be inverted again, since the configuration in this last

stage is an inverter amplifier, which is described by Equation 5.

iout = −

Vout
R10

An important observation is that the resistor R11 in the diagram represents the output,

that is, the brain of the animal, and values considered possible are 1KΩ and 10KΩ, and these

were also considered in the tests. See folder with test files on GitHub for more details.

Figure 8 - Current i1 is the same as current i2 considering an ideal operational amplifier

(5)

(2)

(3)

(4)

(1)

3.2 – BATTERY MONITORING CIRCUIT

In battery powered systems, control of voltage level of the power supplies, to indicate

when to recharge or change batteries is essential. As these are 9 V batteries, this project

established that at 7.5 V it is necessary to change or recharge them. To better understand how

this part of the circuit works, we will go back to analyzing Figure 7.

The responsible for the control of the voltages is the operational amplifier LM741

operating in the comparator configuration. Analyzing each component of the circuit we have:

the 3.3 V zener diode, which is represented by D7, the 1 KΩ R17 resistor that limits the current

in the zener diode, the 470 Ω R18 resistor that limits the current in the D8 led. The resistor value

of 100 KΩ of R15 was chosen so that the current of the circuit was low, improving the efficiency

of the circuit. Given the choices made, it is now possible to determine the value of resistor R16

through equation 3 and 4, considering the threshold of 7.5 V and the comparison value of the

zener diode of 3.3 V.

Being 4 batteries in 7.5 V, we have 30 V, like this:

R16
R16 + R15 =

3.3
30

Doing y = R15 = 100KΩ and we find x:

30(R16) = 3.3(R16) + 3.3(100K)

R16 = 12,36 KΩ

The closest commercial value is 12 KΩ, which is exactly the value used in this project for

R16. Therefore, the D8 led will rise when the battery voltage is below 7.5 V. This is easy to

understand, while the voltage in the zener is less than the voltage over resistor R16, the output

of the LM741 is zero, when the voltage of the zener to be greater than the voltage drop over

R16, the output is activated.

3.3 – CONNECTING THE BATTERIES

It is necessary to use 4 different voltages, namely: +18 V, -18 V, -9 V and +9 V, in addition

to the reference point. The +9 V and -9 V voltages are necessary to supply the amplifiers that

generate the waves and make them go down (AP1 and AP2). The +18 V and -18 V voltages feed

the AP3 converts voltage to current, which demands larger voltage amplitudes, considering

maximum output current amplitudes and tissue impedance. For instance, to apply 1200 µA to a

10 KΩ output impedance, an amplitude voltage of 12 V is needed which is within our voltage

compliance.

(6)

(7)

The maximum supply voltage of the TL072 is exactly +18 V and - 18 V. According to the

manufacturer’s datasheet, values are higher may damage the circuit (see datasheet of the

maximum voltage and current values of the TL072). These values were chosen so that it is

possible to generate all 23 electrical currents of the project. Next in Figure 9, there is the correct

way to connect all 9 V batteries in series to obtain all the necessary supply voltages.

Figure 9 - Connection of 9 V batteries

# CHAPTER 4

### CONSTRUCTION OF THE POWER SHIELD AND RESISTOR BOARD

After understanding how the circuit works, we are able to start building the Open Stim

stimulator. The first step is to build the power shield. For that, it is necessary to access the file

on the GitHub PCB. Inside the PCB folder, look for the Eagle folder, and then Shield. The files are

in that folder and can be changed if necessary. If you prefer not to make any changes, inside the

PCB folder there is the print folder, with PDF file ready to print to use for PCB manufacturing.

### 4.1 – SHIELD

Figure 10 shows the PCB schema file to be used for making the shield PCB. Print the

shield scheme on a laser printer and photo paper and follow the steps below.

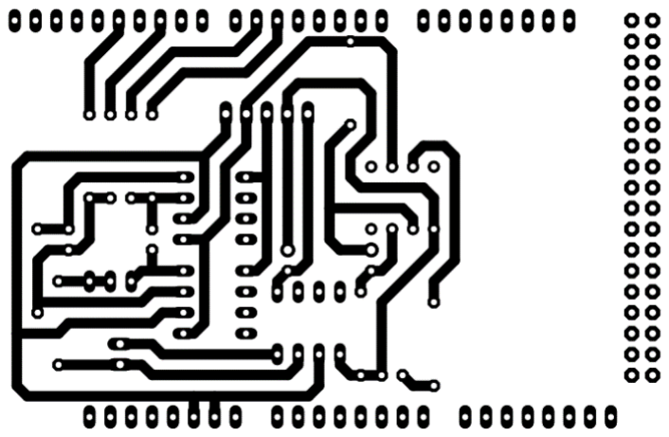
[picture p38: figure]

Figure 10 – PCB Shield

1) Cut the sheet of phenolite or copper-plated fiberglass (we recommend fiberglass due to

frequency interference) to the size of the shield, but leaving 3 mm more on each side, so that

the tracks are not too close to the end the board.

2) After cutting, and with the printing in hand, place the printed side facing the copper plate, as

shown in Figure 11.

Figure 11 - Centered drawing on copper plate

3) Center the design on the plate and secure it with tape so that it does not move. With an cloth

iron, and without using steam, we will transfer the design to the plate. Place the iron at an

average temperature, around 120º C, also place a cloth that can be heated, such as mesh, for

example, on the photographic paper, so that it does not come in direct contact with the iron.

With the iron heated, wipe over the cloth, heating the plate. Pass it in slow movements, applying

for 10 seconds and remove for 5 seconds. Repeat this step for 4 or 5 times, until you notice that

the drawing has been transferred to the plate, as in the example in figure 12.

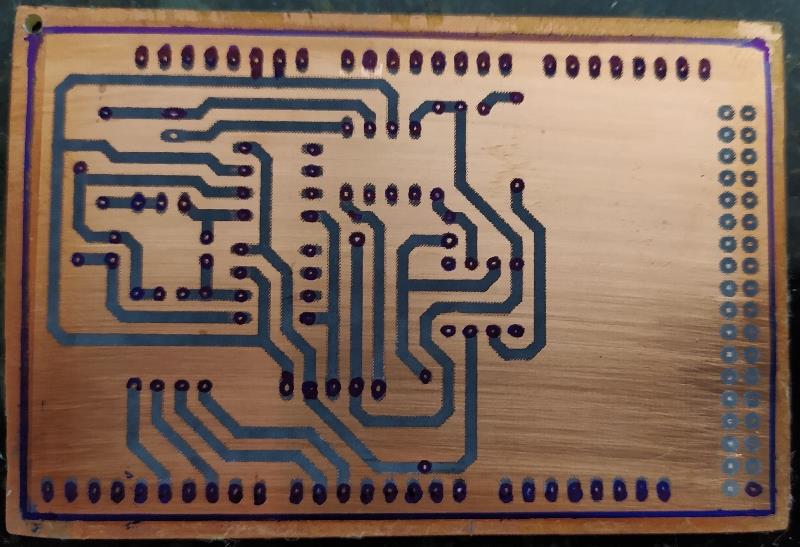
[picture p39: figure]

Figure 12 - Transfer of the printed design to the copper plate

4) After verifying the transfer of the file to the board, note if there was no failure, that is, a

broken track. If this happens, complete the trail with an overhead projector pen. After that, with

the iron perchloride in hand, immerse the plate in the solution and wait until the corrosion

process is finished, as shown in Figure 13. The process should take place in 10 minutes if the iron

perchloride is in good condition. Bearing in mind that, iron perchloride should be used in a plastic

container, never in metal.

Figure 13 - Corrosion process in iron perchloride

5) The expected result should be similar to that of Figure 14, which shows the shield tracks. If

there is a problem and the board shows faults in the tracks, it is recommended to do another

one, and not to make any kind of patch or jumper.

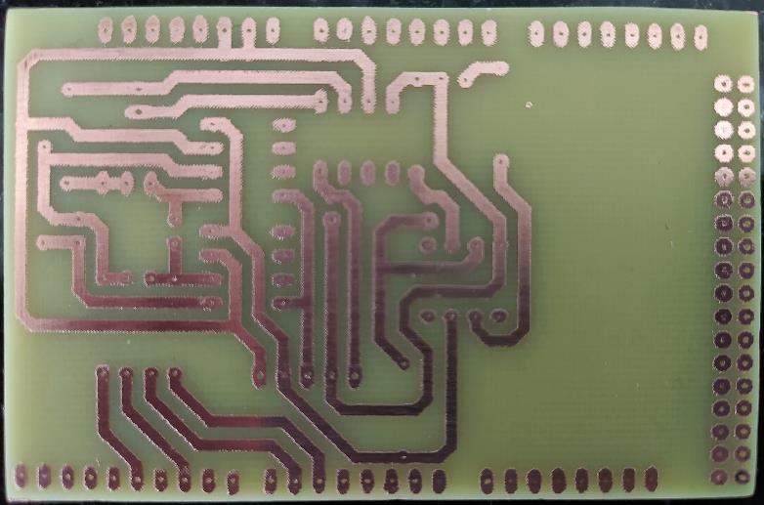
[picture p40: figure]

Figure 14 - Shield tracks after corrosion

6) The next step in the process is to drill the plate so that it can receive the components. Use an

electronic plate punch or drill with a 1 mm bit. At this stage, it may be necessary to count on the

help of one more person or some type of support, in order to avoid wrong holes. To weld the

components in the correct places, use the Eagle schematic.

7) After making all the necessary holes, it is time to weld the components. In this step, a 30 W

soldering iron and a flat-cut plier is recommended for a better finish. If you prefer, also use

solder flux, in order to avoid oxidation at the time of welding. After soldering all components,

clean the plate with isopropyl alcohol with the help of an antistatic brush. The expected result

is similar to that in Figure 15.

Figure 15 - Soldering all components and cleaning the plate

8) After the shield is ready, check visually first, looking for flaws in the weld and poorly fixed

components. If you prefer, you can use a multimeter on the continuity scale and check that

everything is connected according to the project. Then, just fit the shield on the Arduino

Leonardo, checking the connection of all pins. The expected result should be similar to that in

Figure 16 and 17.

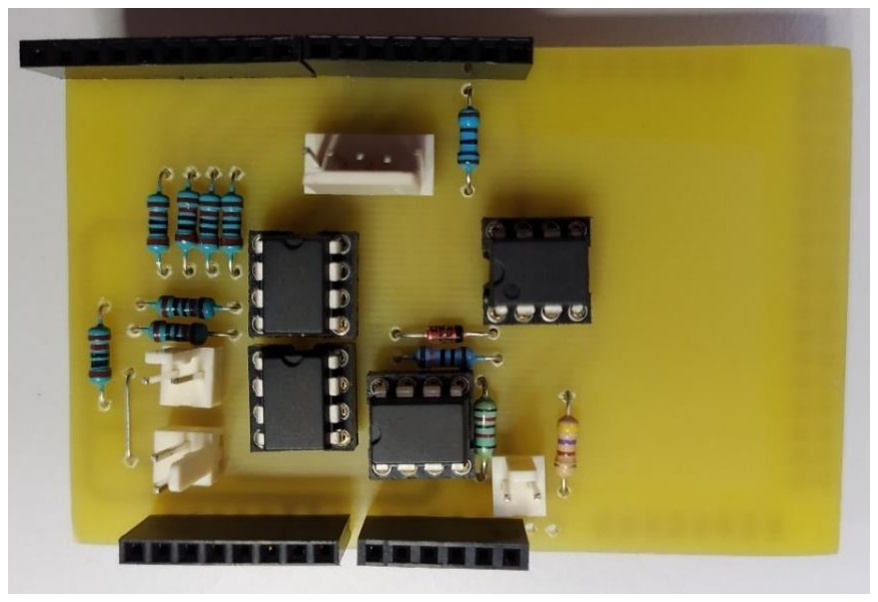
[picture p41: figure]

Figure 16 - Shield finished

Figure 17 - Arduino Leonardo and Shield

4.2 - RESISTOR BOARD

To build the resistor board, follow the same steps for building the shield. Figure 17 shows

the scheme to be printed on a photo paper laser printer.

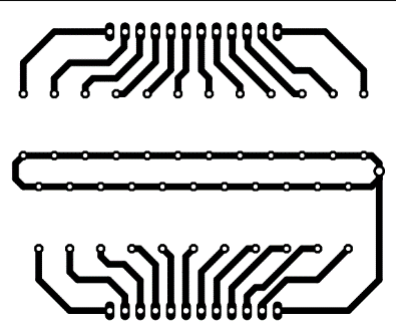
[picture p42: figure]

Figure 17 – PCB resistor board

Following the same order as in the previous steps, Figures 18 and 19 show the expected

results after corroding the resistor plate.

Remember to clean the plate after welding is finished. KK 12-way connectors were used

to facilitate maintenance if necessary. Thus, it is possible to disconnect the resistor board with

ease, preserving the board and preventing it from being removed unnecessarily.

Figure 20 shows the resistor board ready, with only the connection to the wave switch

missing, which will be made later. Table 1 shows the values of the resistances in the sequence

with their respective expected currents. All resistors have 1% tolerance and the male KK

connector is soldered directly on the resistor board, while the female is connected by cables

that connect to the wave switch.

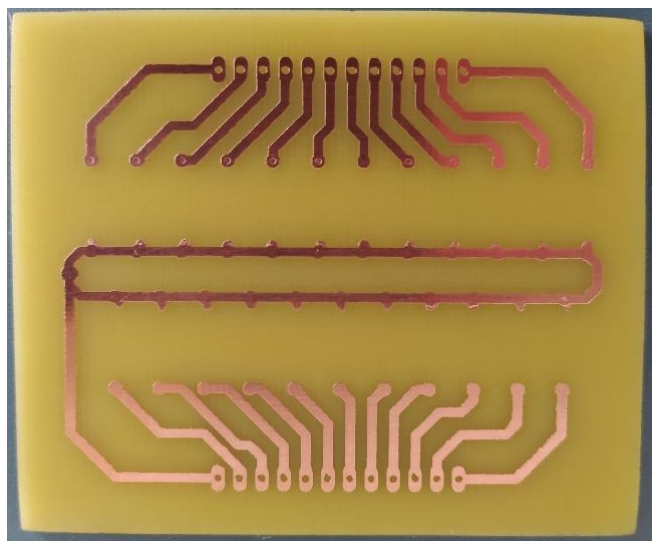
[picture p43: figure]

Figure 18 - Resistor plate tracks after corrosion in iron perchloride

Figure 19 - Component welding

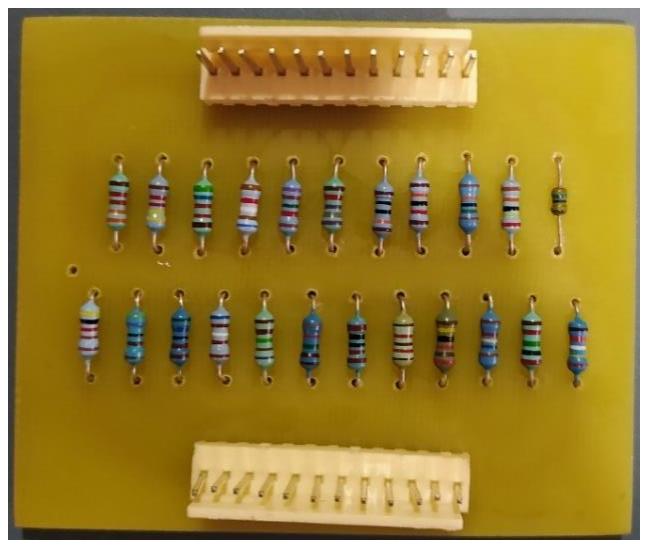
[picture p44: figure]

Figure 20 - Resistor board ready to receive the wave switches

Table 1 - Resistance X Currents

RESISTANCE | CURRENT | RESISTANCE | CURRENT
4,02 KΩ | 1200 µA | 33,2 KΩ | 150 µA
4,7 KΩ | 1000 µA | 44,2 KΩ | 100 µA
5,6 KΩ | 900 µA | 56,2 KΩ | 90 µA
6,19 KΩ | 800 µA | 61,9 KΩ | 80 µA
7,15 KΩ | 700 µA | 71,5 KΩ | 70 µA
8,25 KΩ | 600 µA | 78,7 KΩ | 60 µA
10 KΩ | 500 µA | 100 KΩ | 50 µA
12,1 KΩ | 400 µA | 120 KΩ | 40 µA
14 KΩ | 350 µA | 150 KΩ | 30 µA
16,9 KΩ | 300 µA | 240 KΩ | 20 µA
20,5 KΩ | 250 µA | 360 KΩ | 15 µA
24,9 KΩ | 200 µA

4.3 - ROTARY SWITCHES OR WAVE SWITCHES

Rotary switches are responsible for choosing currents. As we already have the resistor

board ready, we will connect the switches to the board. For this, it is necessary to use flexible

cables. For this project, we recommend the AWG 26 cable. Each rotary switch, Figure 21, has 12

connection pins and a central pin which is the common pin.

Figure 21 - 12 position rotary switch

To connect all resistors to the rotary switches, follow the steps below:

1) First solder the two 12-way male KK connectors at their locations, as shown in Figure 22.

Figure 22 - Welding of 12-way male KK connectors

2) Looking at the resistor plate, locate the last resistor, that is, the 360 KΩ resistor, it will be the

first, because it generates the lowest current. With a 25 cm cable in hand, solder the 12-way female KK connector to the first position that will be connected to the male KK connector for

this 360 KΩ resistor. At the other end of the cable, solder the first position of the rotary switch.

3) Do this until the 11th current, soldering the second resistor which is the 240KΩ on the second

pin of the rotary switch, and so on until the 11th resistor, which is 33,2KΩ. No resistor will be

welded to the 12th pin, once it will be used for the connection between the two switches. To

make this connection, weld the 12th pin of rotary switch 1 to the common pin of rotary switch

2. In this way, the last position of switch 1, enables switch 2.
4) Now with switch 2, continue soldering the resistors from the 12th to the 23rd, that is, 12

resistors ranging from 24.9KΩ to 4.02KΩ, as shown in Figure 23.

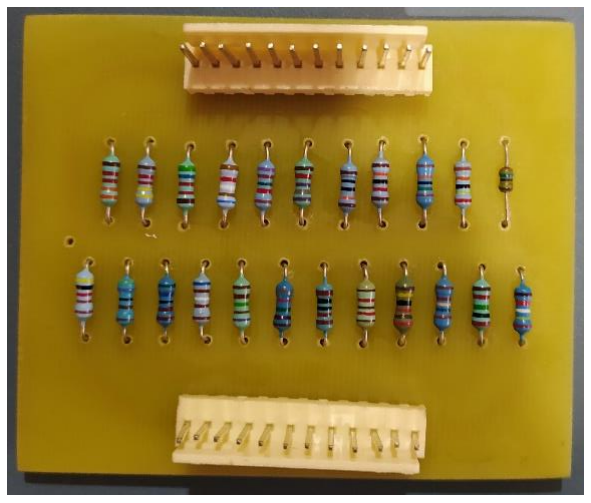
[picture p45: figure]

Figure 23 - Resistor board

5) Figure 24 shows the result after welding on the rotary switch and Figure 25 shows what the

12-way female KK connector will look like.

Figure 24 - 12 position rotary switch with connections made

Figure 25 - Female Kk connector with connections made

NOTE: To use the KK connector, you need the Molex 5051 Type KK connector terminal, which is

shown in Figure 26. The Molex goes inside the female KK connector, which when connected to

the male, completing the connection of the circuit.

Figure 26 - Molex 5051 Type KK Connector Terminal

6) The resistor board has a hole that still does not have a connection, as shown in Figure 27. This

hole is the common one on the resistor board and will be connected directly to the shield. The

resistor board corresponds to resistor R10 in the diagram in Figure 7, so we must connect it in

place. For that, we have to connect two points to the shield, one of them is exactly that common

point of the resistor board, as already said, and the other is the common pin of the rotary switch

1. Figure 28 represents this connection in a simplified way. Here we use less resistors, but the

purpose is to show how the connection between switch 1 and switch 2 is made and also how

the output that will go on the shield is, where the resistor R10 would be.

Figure 27 - Common connection point: Connected to output

Figure 28 - Connection of rotary keys: interconnection between keys

To connect the resistor board to the shield, the 2-way female KK terminal must be used.

The process is the same as previously done using the molex connectors, however, now with only

two ways, which is the output of Figure 28.

# CHAPTER 5

### 3D PRINTING OF THE OPEN STIM BOX

To print the box that will accommodate all circuits, go to the 3D printing folder in the

GitHub directory and locate the .STL files, if you want to update the drawing, include some text

or modify what you think is necessary. There are two ways for this: using the SketchUp software

version 2020 or using SolidWorks.

There are two separate pieces for printing: the first is the box and the second is the lid.

The box has an average printing time of 17 hours while the lid has an average time of 5 hours.

The PLA used is 175 mm in white and black, but this is the user's choice. The brands of our lab

and institution (LINNce/UFSJ) are not in the 3D printing files and have been inserted in this

documentation only as a means of advertisement and credit. You do not need to include them

in your build or derivations.

5.1 – BOX

Figure 29 shows the box seen from the skechtUp software, here it is possible to edit the

drawing and generate the .STL files again. It is important to remember that for this, SketchUp

needs an extension that makes it possible to export the files in the .STL format. Inside the GitHub

directory, in the 3D printing folder, look for the SketchUp folder and inside that folder look for

the Extension for STL - SketchUp folder, and install normally using the software.

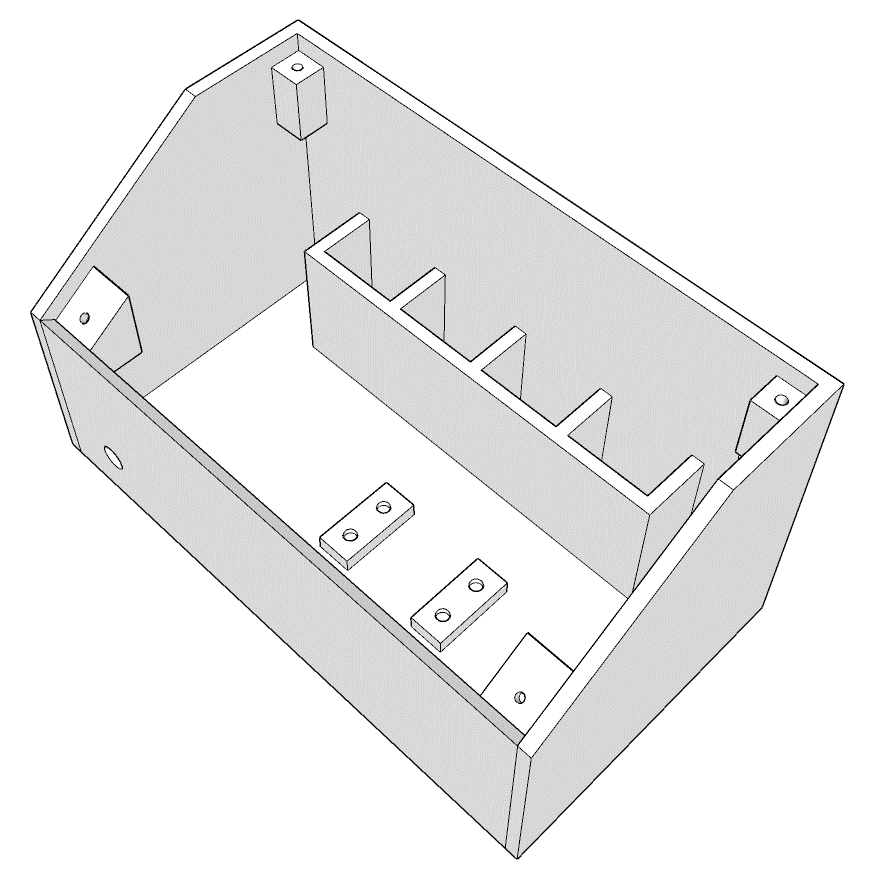
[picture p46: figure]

Figure 29 - Open Stim Box

5.2 - BOX COVER

Figure 30 shows the cover of the box, it is there that the Nextion screen will be

accommodated, as well as the low battery indication led and the two rotary keys, in addition to

the screws that close the cover on the box. It is up to you to put some text to be printed. There

is no such text in the files provided.

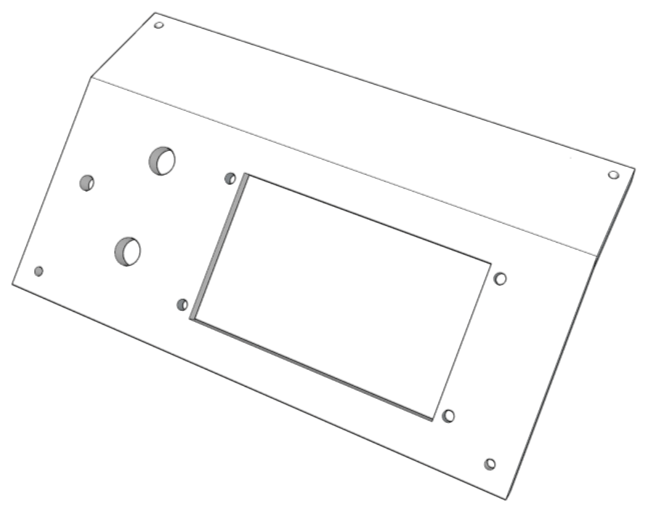
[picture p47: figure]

Figure 30 – Cover Box

5.3 - FINAL PRINTED VERSION

After editing files, configuring the 3D printer and with the .STL files ready, just wait for

the parts to be printed. Figure 31 shows a printed model of the Open Stim box. Figure 32 shows

the printed version of the cover, with text on the top of the cover, identifying the university and

laboratory responsible for printing.

Figure 31 - Print version of the Open Stim box - UFSJ / LINNce

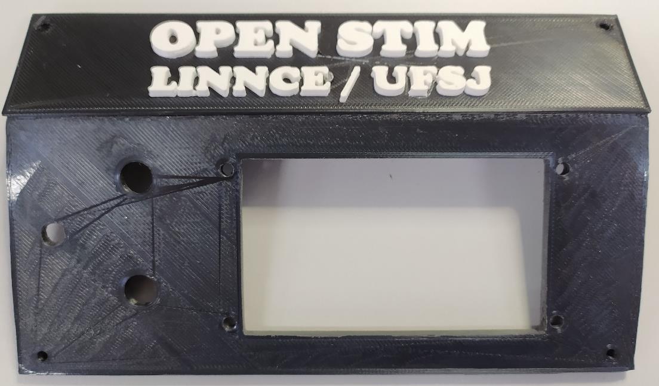
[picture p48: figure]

Figure 31 - Printed version of the Open Stim cover - UFSJ / LINNce

# CHAPTER 6

### CODE: DISPLAY NEXTION AND ARDUINO

All the codes for the Arduino Leonardo, as well as the Nextion display are in the GitHub

directory. In the root folder, look for the Nextion code to access the code for the Nextion screen

model NX4024T032 of 3.2 ". Look for the Arduino coded folder, to access the files needed to

compile and load the code on the Leonardo arduino.

6.1 - NEXTION DISPLAY

The Nextion display is a touch screen that functions as an HMI (man-machine interface).

It is there that the values of frequency, pulse width and selection of positive and negative pulses

will be made. The first step is to download the Nextion Editor software through the link:

https://nextion.tech/nextion-editor/ .

After installation, in the given directory, open the file Nextion_Open_Stim. It is possible

to edit the content, to get to know the names of the variables, change images, change values,

positions, etc. In short, it is possible to modify the entire layout if deemed necessary. However,

when there is any change, it is necessary to check the address of the variable, so that the

necessary adjustments are made in the Arduino code. Figure 32 shows the first screen to be

displayed, showing the information of the authors who developed the equipment and the university. This screen will appear for a few seconds and then advance to the main menu

automatically. This second screen is shown in Figure 33.

Figure 32 - First Nextion display screen

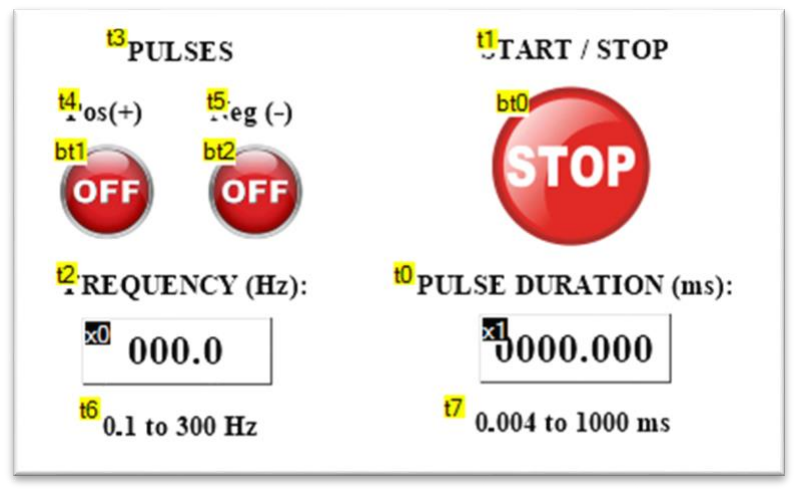
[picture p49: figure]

Figure 33 - Nextion main display menu

The Nextion screen has its own programming, so we suggest that before any

modification, consult the manufacturer's guide to clarify doubts and get to know the display.

This can be done using the link: https://nextion.tech/editor_guide/. It is also possible to access

all available functions at: https://nextion.tech/instruction-set/ .

To decrease the brightness of the screen and increase the equipment's autonomy, the

DIMS function was used. With it, it is possible to define the brightness of the screen in percentual

term. For this project it was set to 40%, therefore, the function is as follows: DIMS = 40. With

this value, the current is approximately 36 mA. With this value, the current is approximately 40

mA. The function must be entered in the Preinitialize Event field on the second screen, that is,

on the main screen, as shown in Figure 34.

Figure 34 - Inserting DIMS function to control the brightness of the screen

After making all or any modifications you deem necessary, you must send the file to the

Nextion screen. A memory card of up to 32 GB formatted in FAT32 is required for this. To

generate the file that will be saved on the memory card, go to the File menu and click on TFT file

output, as shown in Figure 35. Then, choose the location of the memory card to save the TFT

file.

Note: It is necessary to save the file outside any folders and at the root of the memory card.

With the file saved on the microSD card, just insert it into the slot on the Nextion screen,

shown in Figure 36. After the card is already inserted, supply the screen with 5 VDC, as shown

in Figure 37, as soon as the power is turned on, file upload will start, and it will be saved in

Nextion non-volatile memory. When the upload is finished, just turn off the power and remove

the microSD card and the code and layout are saved. If you need to modify something in the

Nextion Editor, repeat the process described above and upload the TTL file again, so the previous

one will be replaced by the new one.

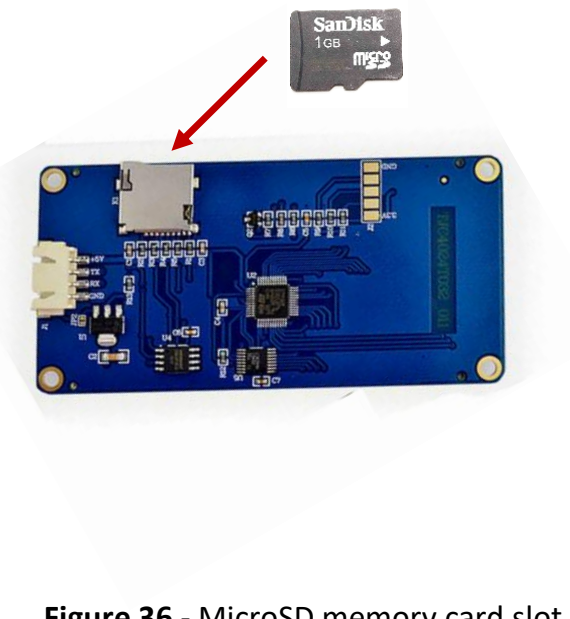
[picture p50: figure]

Figure 35 - Exporting TFT file | Figure 36 - MicroSD memory card slot

Figure 37 - Power 5VDC display Nextion

There is another upload option, which is using the USB to TTL adapter. The connection

to be made at the adapter terminals is shown in Figure 38. The transfer is made directly from

the Nextion Editor to the memory of the Nextion display, eliminating the use of the microSD

card.

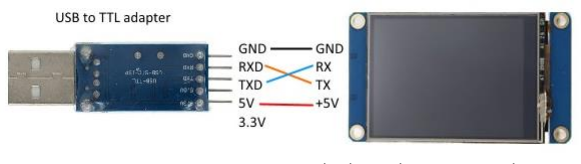
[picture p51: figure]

Figure 38 - Connection on Nextion display with USB to TTL adapter

During the sending of the file, either by MicroSD or by the TTL Adapter, observe the

percentage of sending and then the success message in the upload, as shown in Figure 39, to be

sure that the file was sent without errors.

Figure 39 - Upload display Nextion

Next, a summary of the main screen of the Nextion Editor software will be made in

Figure 40, to assist in understanding along with the documentation informed in the links above.

It is essential that the user studies and practices before making changes to the project. Make all

tests, like turning on and off a led, controlling a potentiometer writing a message on the screen,

etc.

Figure 40 - Main screen Nextion Editor

1) Main Menu
2) Toolbars
3) Toolbox Pane
4) Design Canvas
5) Page Pane
6) Picture Resource Pane
7) Non Visual Components
8) Output
9) User Event Code
10) Attributes Pane
11) Status Bar

6.2 - ARDUINO LEONARDO

First step is to download the Arduino IDE software through the link:

https://www.arduino.cc/en/software. Install the program, but before opening for the first time,

it is necessary to include the Nextion library in the Arduino Library. To do this, follow the steps

below:

1) Inside the GitHub directory, look for the folder Arduino Code, and inside that folder you will

have the folder: ITEADLIB_Arduino_Nextion-master. Download it.

2) Copy the folder ITEADLIB_Arduino_Nextion-master and paste it in the location: C: \ Program

Files (x86) \ Arduino \ libraries, that is, in the installation location of the Arduino IDE version 32

bits, library. Figure 41 shows what the library folder looks like after the above process.

3) In Figure 42 we have the library already included. To check, open the Arduino IDE, click on the

Sketch menu and then Add Library. In the window that opens, check if it appears at the end,

after all the other standard Arduino libraries.

It is now possible to compile the Arduino Leonardo code. To open the code, access the

directory on GitHub and open the folder Arduino Code. Inside it, open the folder

Arduino_Open_Stim and inside it you will find the file that must be uploaded to the Arduino

Leonardo.

The Arduino Leonardo documentation was made available in chapter 2 of this Manual.

The ports used for communication with the Display Nextion are 0 and 1 (RX and TX, respectively).

All connections will be explained and detailed in the next chapter.

Now it is important to have the Nextion screen ready and programmed, and with the

Arduino also loaded with the available code.

Figure 41 - Arduino library folder after adding the Nextion display library

Figure 42 - Verification of inclusion of the Nextion library by the Arduino IDE

Remembering again that, in case of modification in any part of the code, whether in

Arduino or Nextion, it is necessary to check in both codes if the changes are in agreement, if

what has been changed in one will not affect the other and if it does, the necessary modifications

are already made for both codes / programming. Regarding the code, all explanations are given

directly in the code, in the form of comments.

# CHAPTER 7

### ASSEMBLING THE OPEN STIM

Before starting the actual assembly, it is recommended to make a Check List of materials and tools:

7.1 - CHECK LIST MATERIALS AND TOOLS

- Flush cutting pliers
- Nose pliers
- Welding suction
- Soldering Iron
- Tin / lead solder
- Multimeter
- Clean contact or Isopropyl Alcohol
- Drill with set of drills
- Stylus
- Screwdriver 1/8 x 3"
- Philips key 1/8 x 3"
- Brush tool
- Double-sided tape

These are the basic tools. However, the user can feel free to use other tools, from the

simplest to the most sophisticated. In this final assembly part, two people are recommended,

one as the main technician and the other as an assistant.

7.2 - MOUNTING THE BATTERIES IN THE HOUSING

Go back to Figure 9 and connect the 4 batteries according to the diagram shown. To

do this, use item 8 of the material list (the material list is also in the GitHub directory, in the root folder), which is the 9 V battery clip. After the connection between the terminals has been made,

you can place the batteries in the box in their respective places, as shown in Figure 43.

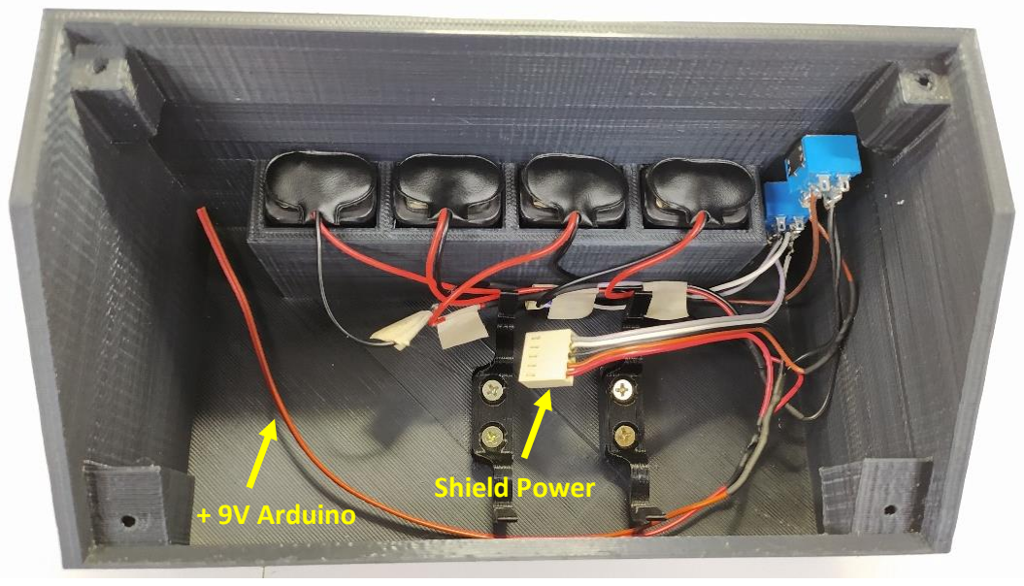
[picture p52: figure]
+ 9V Arduino; Shield Power

Figure 43 - Connection of batteries and lever switches

Now it is necessary to exit the lever switches and supply the shield, for this, we will

use the 5-way female KK connector, since the male is already soldered on the shield. As

previously done, it is necessary to use the Molex terminal, item 20 of the bill of materials. The

sequence from left to right is:

1) Reference
2) -9 V
3) +9 V
4) -18 V
5) +18 V

Figure 44 - 5-way female KK connector for shield power

Still on Figure 43, we can also fix the Arduino Leonardo support, using the flat head screw

2.2 x 6.5 mm, which is item 55 in the list of materials, while the support is item 54. To fix, use

the philips wrench and a medium torque, to avoid breaking the support that is made of PVC.

And finally, take + 9 V in parallel to power the Arduino with the male P4 plug, item 19 of the list

of materials. The yellow arrows in Figure 43, indicate the points mentioned above in case of

doubt.

Now, attach the shield to the Arduino, as in Figure 45 and attach it to the bracket that

was previously fixed. Just press down lightly and the bracket will embrace the Arduino.

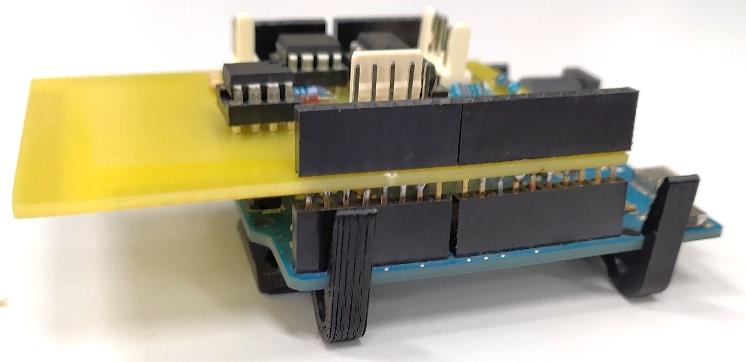
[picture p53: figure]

Figure 45 - Arduino + Shield

For now, let's leave the box aside and mount the lid with the Nextion screen. The first

step is to fix the Nextion screen to the cover. For that, use the 4 screws with nut, item 57 of the

bill of materials. Check if it is well fixed, but without overtightening the screws, avoiding damage

to the display and also to the cover. Figure 46 shows how it should look.

Figure 46 - Nextion display attached to the housing cover

Next, fix the two rotary keys, both are accompanied by their nuts, so pass the key from

the inside out, insert the nut and tighten it until the key does not move when used. If you prefer, use 2.5 x 100 mm nylon cable ties to better finish the cables that go to the resistor plate, as

shown in Figure 47. Do not bend the cables too much, do not make sharp bends and also avoid

mechanical stress in the cable close to the welding site.


Figure 47 - Attaching the two rotary keys to the housing cover

With the keys in place, place the 3 mm led holder, item 17 on the bill of materials. Then,

place the LED inside the holder. Also place the two knobs on the rotary switches, item 9. Figure

48 shows how it looks after these steps.


Figure 48 – Inserting led and knobs

It is also possible to fix the resistor plate. With the box at the front, the board will be on

the right side, since the left most is the shielded Arduino. Glue the double-sided tape to the ends

of the board, being careful not to stick it on the tracks and fix it on the left side of the box, as

shown in Figure 49.

Figure 49 - Fixing the resistor plate to the box

Now solder the ends of the Led with the same AWG 26 cable, and at the other end solder

the Molex terminal to be inserted into the 2-way female KK connector, as this will be connected

to the shield. Pay attention to the polarity of the led. If necessary, refer to the diagram again.

Figure 50 shows where the female KK connectors for all connections should be placed.

Output; Shield Power; Resistor Bar

Figure 50 - Shield connections

### Led

Remember to connect the current selection rotary switches to the resistor board. As

shown in Figure 51.

Figure 51 - Connection of rotary switches to the resistor plate

Among the connections to the shield, only the output connection, represented in the

diagram by resistor R11, is missing. For hits we will use the female RCA connector, item 5 of the

material list, Molex terminal, two-way female KK connector and 20 cm of the AWG 26 cable. This

cable must already be placed, being one end into the box for connection in the shield and other

end out of the box for connecting the RCA, since the RCA can only be fixed in the box from the

outside to the inside. At one end, and with the help of another person or some support, solder

the RCA connector, paying attention to the polarity. At the other end, solder the Molex terminal

to the two-way female KK connector. After welding, fix the RCA connector to the box, Figure 49

shows what the final result looks like. Finally, connect the output and all other connections to

the location shown in Figure 52.


Figure 52 - Output: RCA connector

The last step is to connect the Nextion screen and communicate with the Arduino. It's

very simple: supply the Nextion screen with 5 VDC from the Arduino itself. Then connect the TX

of the Nextion screen to the RX of the Arduino Leonardo and the RX of the Nextion screen to the

TX of the Arduino Leonardo. Logically, this connection is made by the shield, which gives access

to the pins of the Arduino Leornado through the female connector bar. Figure 53 shows how

this connection is made.

Figure 53 - Connection between Arduino Leonardo and Display Nextion

Turn on the two lever switches to test the equipment, the Arduino Leonardo leds

should indicate the energization and the Nextion screen must initialize. If the batteries are

under 7.5 V the indication LED will also be on, as shown in Figure 54.


Figure 54 - Open Stim finished

The stimulator is ready, but it is necessary to fully test it. To proceed to the tests, go to

the GitBub directory and look for the Tests folder. There you will find a guide to help in the tests

and verification of the functioning.

# FINAL CONSIDERATIONS

The Laboratory of Neuroengineering and Neuroscience - LINNce of the Federal

University of São João del-Rei - UFSJ, hopes that, with this equipment, you can start or continue

your research inside or outside a university or technical school. We appreciate your interest in

getting to know our stimulator and we count on your contributions to improve the project

through GitHub. See you soon and good studies!

# ACKNOWLEDGMENTS

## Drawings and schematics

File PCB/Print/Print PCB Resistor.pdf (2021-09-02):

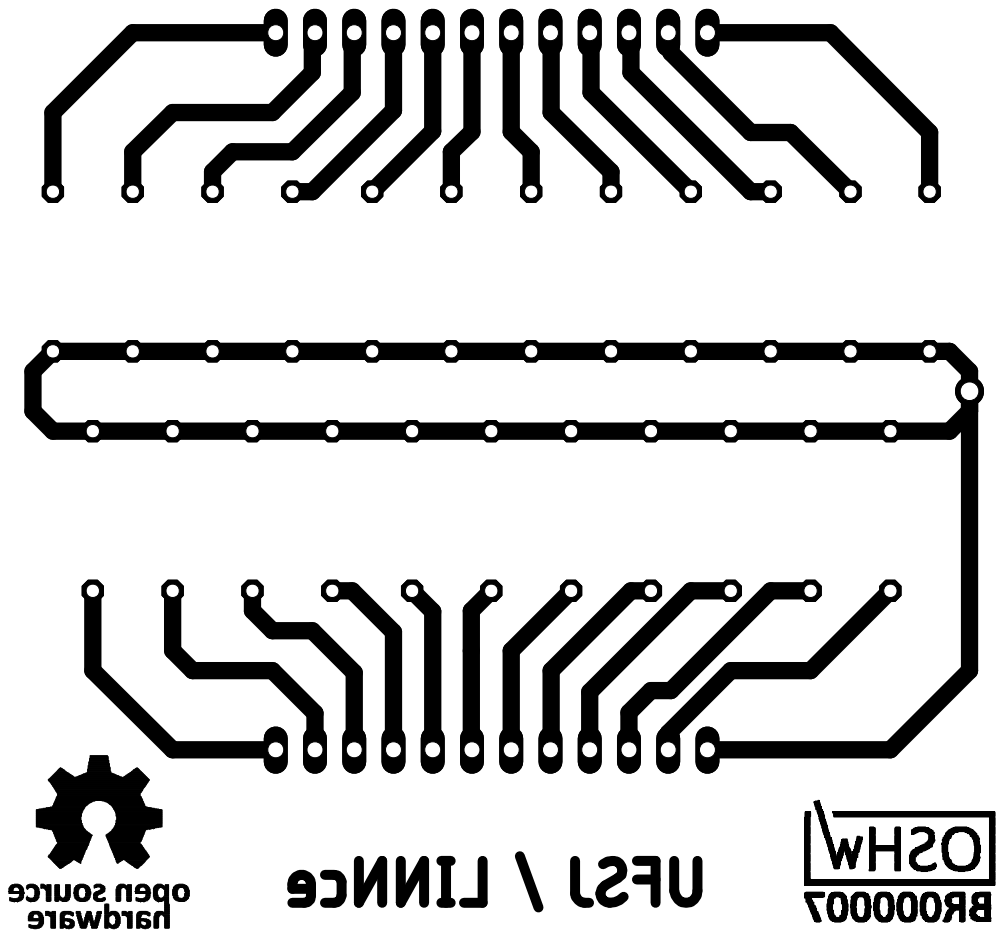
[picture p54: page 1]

02/09/2021 11:54 C:\Users\Maikon Lorran\Desktop\Eagle\Resistor Board\PCB Resistor Board.brd

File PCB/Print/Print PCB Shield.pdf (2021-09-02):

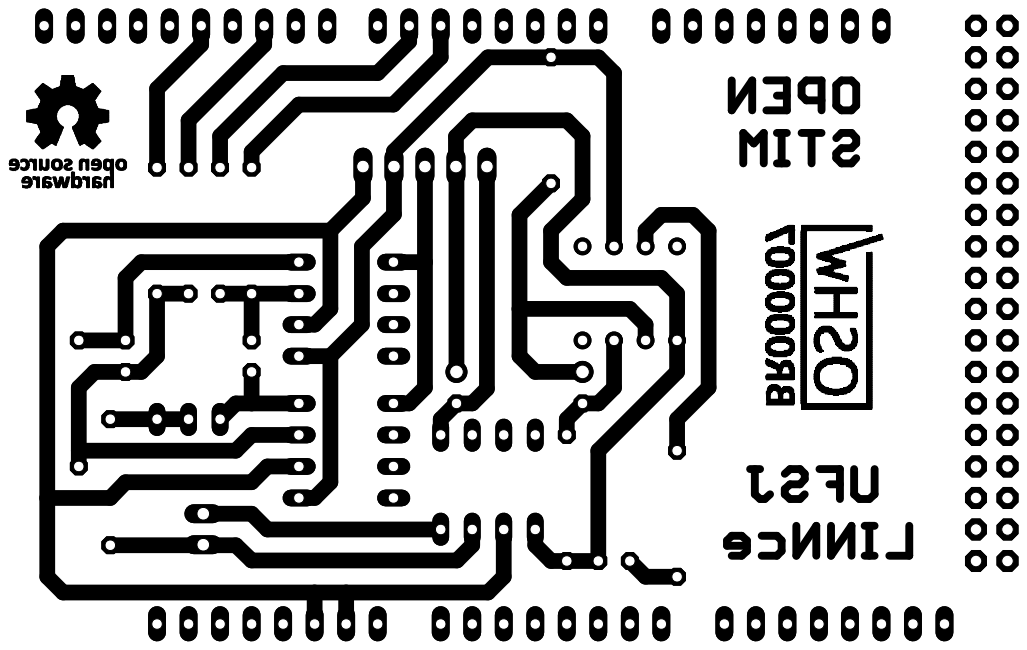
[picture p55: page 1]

02/09/2021 11:57 C:\Users\Maikon Lorran\Desktop\Eagle\Shield\Shield_PCB.brd

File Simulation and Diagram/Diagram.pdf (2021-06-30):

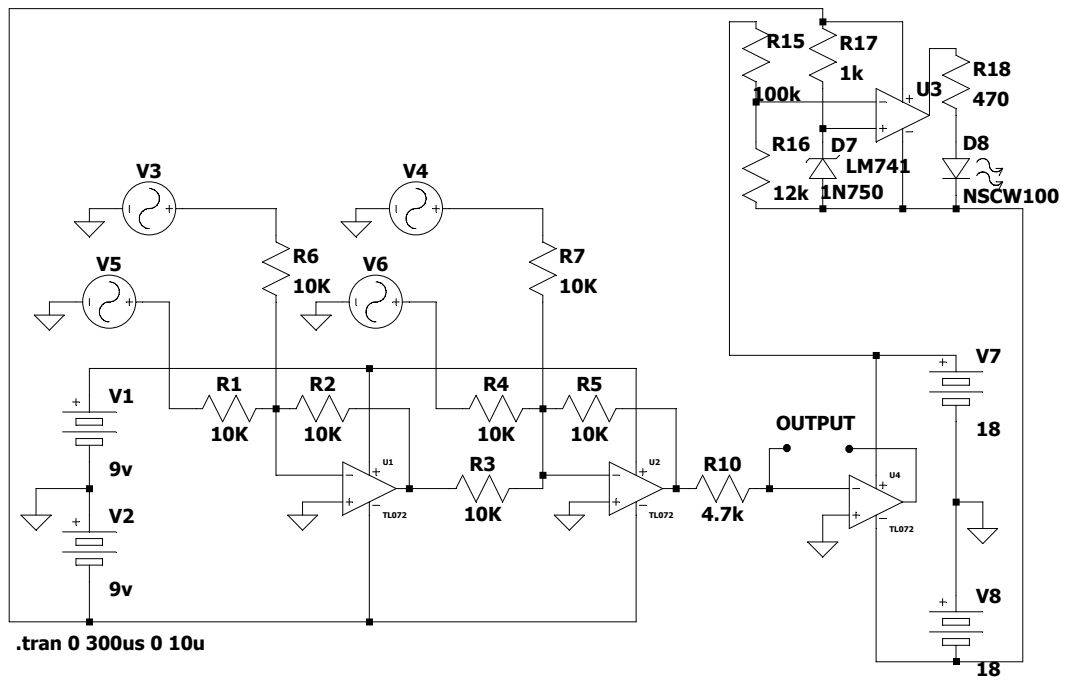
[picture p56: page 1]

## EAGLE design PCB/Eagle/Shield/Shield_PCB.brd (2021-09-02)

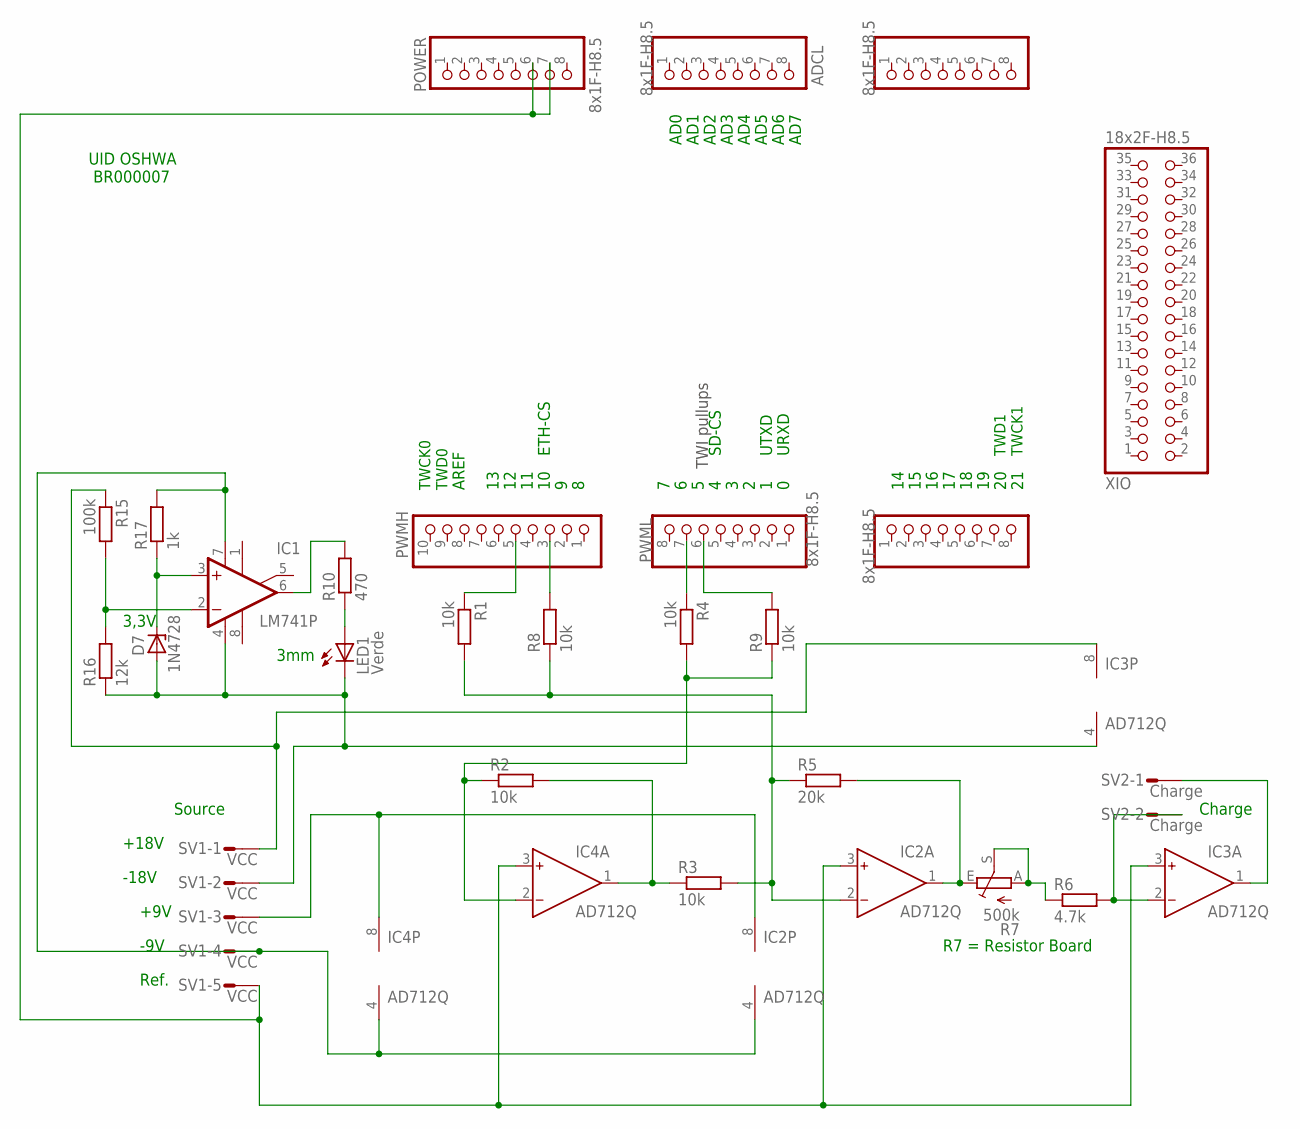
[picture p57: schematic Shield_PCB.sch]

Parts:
ADCH: 8x1F-H8.5; 1X08
ADCL: 8x1F-H8.5; 1X08
COMMUNICATION: 8x1F-H8.5; 1X08
D7: 1N4728; DO41Z10
IC1: LM741P; DIL08
IC2, IC3, IC4: AD712Q; DIL08
LED1: Verde; LED3MM
POWER: 8x1F-H8.5; 1X08
PWMH: 10x1F-H8.5; 1X10
PWML: 8x1F-H8.5; 1X08
R1, R2, R3, R4, R8, R9: 10k; 0207/10
R5: 20k; 0207/10
R6: 4.7k; 0207/10
R7: 500k; B64Y
R10: 470; 0207/10
R15: 100k; 0207/10
R16: 12k; 0207/10
R17: 1k; 0207/10
SV1: VCC; L05P
SV2: Charge; L02P
XIO: 18x2F-H8.5; 2X18

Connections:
unnamed: IC4.2 (IN-), R2.1, R4.2, R9.1
unnamed: IC4.1 (OUT), R2.2, R3.1
unnamed: IC2.2 (IN-), R1.2, R3.2, R5.1, R8.1
unnamed: IC2.1 (OUT), R5.2, R7.E
unnamed: IC3.2 (IN-), R6.2, SV2.2
unnamed: R6.1, R7.A, R7.S
unnamed: IC3.1 (OUT), SV2.1
unnamed: PWMH.3, R8.2
unnamed: PWMH.5, R1.1
unnamed: PWML.7, R4.1
unnamed: PWML.6, R9.2
unnamed: IC3.8 (V+), R15.1, SV1.1
unnamed: D7.A, IC1.4 (V-), IC3.4 (V-), LED1.K (C), R16.1, SV1.2
unnamed: IC1.7 (V+), IC2.4 (V-), IC4.4 (V-), R17.2, SV1.4
unnamed: IC2.3 (IN+), IC3.3 (IN+), IC4.3 (IN+), POWER.6, POWER.7, SV1.5
unnamed: D7.C, IC1.3 (+IN), R17.1
unnamed: IC1.2 (-IN), R15.2, R16.2
unnamed: IC1.6 (OUT), R10.2
unnamed: LED1.A, R10.1
unnamed: IC2.8 (V+), IC4.8 (V+), SV1.3

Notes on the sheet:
TWI pullups
TWCK1
TWD1
TWCK0
TWD0
AD1
AD2
AD3
AD4
AD5
AD6
AD0
AREF
AD7
SD-CS
UTXD
URXD
ETH-CS
Source
Charge
R7 = Resistor Board
3,3V
3mm
+18V
-18V
+9V
-9V
Ref.
UID OSHWA BR000007

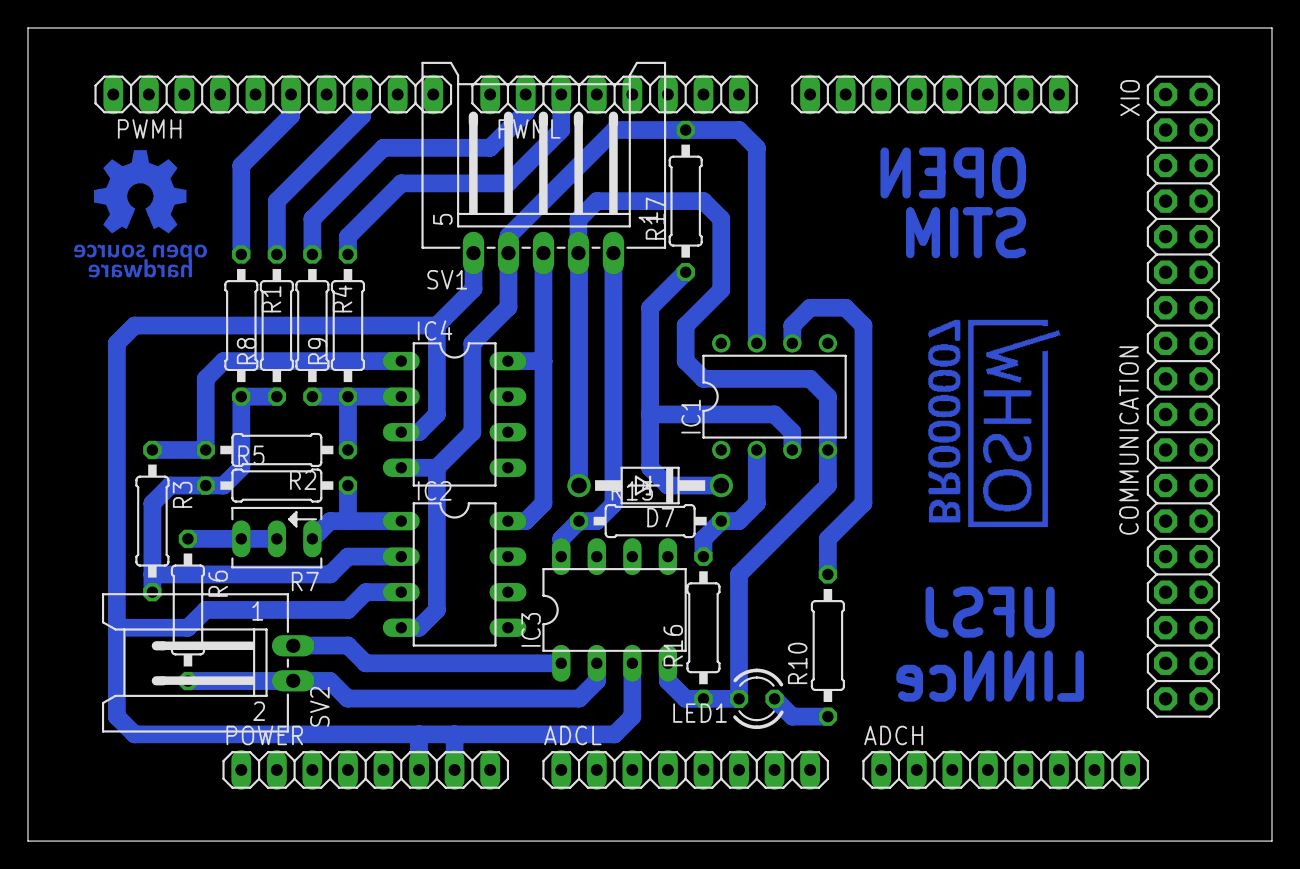
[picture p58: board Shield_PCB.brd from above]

Board: 2 copper layers, 88.9 x 58.1 mm, 28 parts (0 on the bottom side), 20 nets.

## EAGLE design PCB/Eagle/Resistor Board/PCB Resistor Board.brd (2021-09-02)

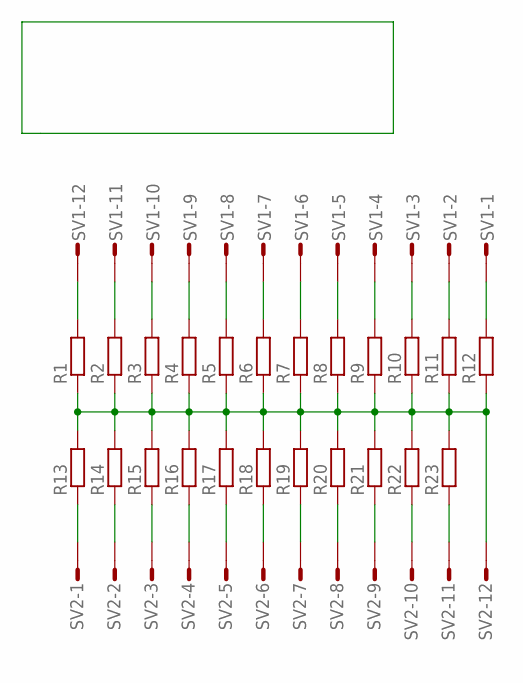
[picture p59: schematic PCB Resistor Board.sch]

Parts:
R1, R2, R3, R4, R5, R6, R7, R8, R9, R10, R11, R12, R13, R14, R15, R16, R17, R18, R19, R20, R21, R22, R23: R-EU_0207/10; 0207/10
SV1, SV2: S12P

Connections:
unnamed: R13.1, SV2.1
unnamed: R14.1, SV2.2
unnamed: R15.1, SV2.3
unnamed: R16.1, SV2.4
unnamed: R17.1, SV2.5
unnamed: R18.1, SV2.6
unnamed: R19.1, SV2.7
unnamed: R20.1, SV2.8
unnamed: R21.1, SV2.9
unnamed: R22.1, SV2.10
unnamed: R23.1, SV2.11
unnamed: R1.2, SV1.12
unnamed: R1.1, R2.1, R3.1, R4.1, R5.1, R6.1, R7.1, R8.1, R9.1, R10.1, R11.1, R12.1, R13.2, R14.2, R15.2, R16.2, R17.2, R18.2, R19.2, R20.2, R21.2, R22.2, R23.2, SV2.12
unnamed: R2.2, SV1.11
unnamed: R3.2, SV1.10
unnamed: R4.2, SV1.9
unnamed: R5.2, SV1.8
unnamed: R6.2, SV1.7
unnamed: R7.2, SV1.6
unnamed: R8.2, SV1.5
unnamed: R9.2, SV1.4
unnamed: R10.2, SV1.3
unnamed: R11.2, SV1.2
unnamed: R12.2, SV1.1

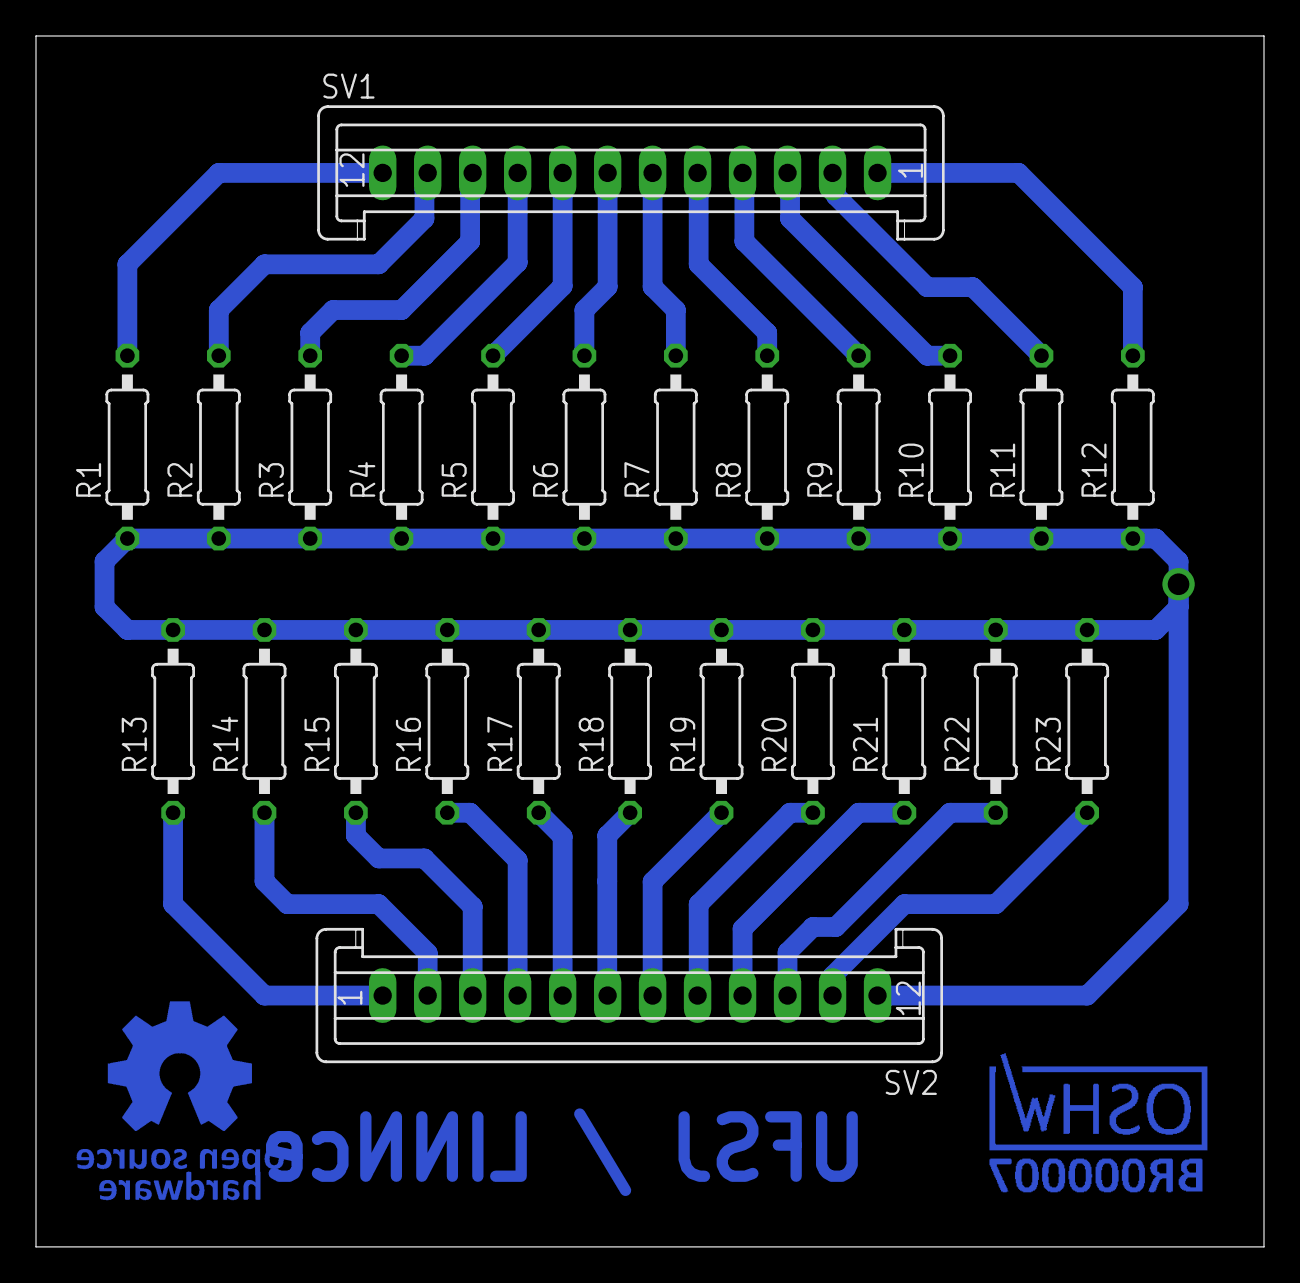
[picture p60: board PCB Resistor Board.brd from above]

Board: 2 copper layers, 68.2 x 67.3 mm, 25 parts (0 on the bottom side), 24 nets.

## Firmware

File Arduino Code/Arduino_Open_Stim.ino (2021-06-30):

/* ===============================================================================

           FEDERAL UNIVERSITY OF SÃO JOÃO DEL-REI - UFSJ 
           GRADUATE PROGRAM IN ELECTRICAL ENGINEERING - PPGEL
           LABORATORY OF NEUROENGINEERING AND NEUROSCIENCE – LINNCE
        
             - OPEN STIM - ELECTRICAL STIMULATOR OPEN SOURCE HARDWARE -

   --> DEVELOPED BY: 

        1. MAIKON LORRAN SANTOS
        2. JOÃO DANIEL NOLASCO
        3. VINÍCIUS ROSA COTA

=============================================================================== */

// --- Auxiliary Library ---

#include  "Nextion.h"   //Nextion library

// ===============================================================================
// --- Display Nextion Object Declaration ---
 
NexDSButton bt0   = NexDSButton(1, 11, "bt0");  // Start / Stop
NexDSButton bt1   = NexDSButton(1, 9, "bt1");  // Positive pulse
NexDSButton bt2   = NexDSButton(1, 10, "bt2");  // Negative pulse
NexNumber x0      = NexNumber(1, 7, "x0"); // Frequency: 0.1 - 300Hz
NexNumber x1      = NexNumber(1, 8, "x1"); // Pulse duration: 0.004 - 1000ms

// ===============================================================================
// --- Hardware Mapping ---

byte pino_OCR4D = 6; // The duty cycle does not vary. Base for positive pulse
byte pino_OCR4B = 10; // Varies work cycle and frequency. Cut the beginning of the wave from pin 6.
byte pino_OCR4D_invertido = 12; // The duty cycle does not vary. Base for the negative pulse.
byte pino_OCR4A_invertido = 5; // Varies work cycle and frequency. Cut the end of the wave from pin 12.
byte pino_OCR4B_invertido = 9; // It is not used but generates PWM
byte pino_OCR4A = 13; // It is not used but generates PWM


// ================================================================================================================
// --- Global Variables ---

uint32_t ds_ST;     // Stores the start / Stop Status
uint32_t ds_P;      // Stores the status of the Positive button
uint32_t ds_N;      // Stores the state of the Negative button

word contador_periodo = 0; // The counter timer 4 of the Arduino Leonardo has a resolution of 10 bits.
word contador_largura_do_pulso = 0; //The counter timer 4 of the Arduino Leonardo has a resolution of 10 bits.

double frequencia_desejada = 0; // 0.1 Hz to 300 Hz per design choice
double largura_do_pulso_desejada = 0; // 0.0004 ms up to 1000 ms per project choice

uint32_t decimal; // Stores the value entered on the Nextion screen
String recebido; // Convert received number to string
double numero_F; // Convert the received number to Double
double numero_D; // Convert the received number to Double

double limite_largura_pulso; // It stores double values temporarily, to reduce the number of calculations.

// =================================================================================================================

/*=================================================================================================
NOTE 1:
 
  1. Pins 6 and 10 generate the positive pulse
  2. Pins 5 and 12 generate the negative pulse
  3. Arduino connection: pins 5 and 6 on the stage 1 op amp and 10 and 12 on the stage 2 op amp

=================================================================================================== =*/

void setup() // DEFINES INITIAL CONDITION

{
  nexInit();  // Initializes Nextion tft display
  Serial.begin(9600); // Communication rate
  TCCR4D = 0b00000000; // The value of this register remains unchanged throughout the code.
}

void loop()
{
  // INFINITE LOOP START: 

  bt0.getValue(&ds_ST); // Start / Stop button
  bt1.getValue(&ds_P); // Positive pulse button
  bt2.getValue(&ds_N); // Negative pulse button
  
  switch (ds_ST)
  {
    
    case 0:
    digitalWrite(pino_OCR4D,LOW); // Pin 6
    digitalWrite(pino_OCR4B,LOW); // Pin 10
    pinMode(pino_OCR4D,INPUT); // Define pin 6 as input
    pinMode(pino_OCR4B,INPUT); // Define pin 10 as input
    digitalWrite(pino_OCR4D_invertido,LOW); // Pin 12
    digitalWrite(pino_OCR4A_invertido,LOW); // Pin 5
    pinMode(pino_OCR4D_invertido,INPUT); // Defines pin 12 as input
    pinMode(pino_OCR4A_invertido,INPUT); // Defines pin 5 as input
    digitalWrite(pino_OCR4B_invertido,LOW); // Pin 9
    digitalWrite(pino_OCR4A,LOW); // Pin 13
    pinMode(pino_OCR4B_invertido,INPUT); // Define pin 9 as input
    pinMode(pino_OCR4A,INPUT); // Define pin 13 as input
    break;
    
    case 1:
    if (ds_P > 0)
    {
      digitalWrite(pino_OCR4D_invertido,LOW); // Pin 12
      digitalWrite(pino_OCR4A_invertido,LOW); // Pin 5
      pinMode(pino_OCR4D_invertido,OUTPUT); // Defines pin 12 as output
      pinMode(pino_OCR4A_invertido,OUTPUT); // Defines pin 5 as output
    }
    else
    {
      digitalWrite(pino_OCR4D_invertido,LOW); // Pin 12
      digitalWrite(pino_OCR4A_invertido,LOW); // Pin 5
      pinMode(pino_OCR4D_invertido,INPUT); // Defines pin 12 as input
      pinMode(pino_OCR4A_invertido,INPUT); // Defines pin 5 as input
    }
    if (ds_N > 0)
    {
      digitalWrite(pino_OCR4D,LOW); // Pin 6  
      digitalWrite(pino_OCR4B,LOW); // Pin 10   
      pinMode(pino_OCR4D,OUTPUT); // Defines pin 6 as output
      pinMode(pino_OCR4B,OUTPUT); // Defines pin 10 as output   
    }
    else
    {
      digitalWrite(pino_OCR4D,LOW); // Pin 6
      digitalWrite(pino_OCR4B,LOW); // Pin 10   
      pinMode(pino_OCR4D,INPUT); // Define pin 6 as input
      pinMode(pino_OCR4B,INPUT); // Define pin 10 as input
    }
    break;
  }
  
  // Reads the entered frequency directly from the Nextion screen:
  
  x0.getValue(&decimal); // x0 stores the frequency value on the Nextion screen
  recebido = String(decimal); // Converts the value to string
  numero_F = recebido.toDouble(); // Converts the value to Double
  frequencia_desejada = numero_F / 10; // Value already in decimal
  if (frequencia_desejada < 0.1) // 0.1 Hz is the lower frequency limit chosen in the project.
  {
    frequencia_desejada = 0.1; // Project limitation
    x0.setValue(1);
  }


  // Read directly from the Nextion screen the pulse duration entered:
  
  x1.getValue(&decimal); // x1 stores the pulse width value on the Nextion screen
  recebido = String(decimal); // Converts the value to string
  numero_D = recebido.toDouble(); // Converts the value to Double
  largura_do_pulso_desejada = numero_D / 1000; // Go to milliseconds.
  if (largura_do_pulso_desejada < 0.004) // The minimum value chosen in the design for the pulse width is 0.004 ms.
  {
    largura_do_pulso_desejada = 0.004; // Project limitation
    x1.setValue(4);
  }
  
  largura_do_pulso_desejada = largura_do_pulso_desejada/1000; // Go from milliseconds to seconds
  limite_largura_pulso = ((1/frequencia_desejada)/2);  // The highest possible value for the pulse width is 50% because the wave generated must be symmetrical. Value in seconds.
 
  //    == END OF BASIC CALCULATIONS ==   //


/*========================================================================================================================================================
NOTE 2:
   With the frequency CLOCK_PRINCIPAL equal to 16 MHz, maximum prescaler value of timer / counter 4 equal to 16384 and PWM resolution of 1023,
   the minimum possible frequency to be generated is ((16000000/16384) / 1023) = 0.96 Hz.
   Thus, in order to generate frequency waves below 0.96 Hz, the delay () and delayMicroseconds () functions need to be used.
   0.06 Hz would be the value reached, if it were possible to divide the clock frequency from the PLL circuit,  which is at its minimum value of 16 MHz,
   at a value less than or equal to 0.1 Hz (limit of the original project).
   That is, if the timer / counter prescaler 4 reached the value of 262144.

 ========================================================================================================================================================= =*/
 
  // FREQUENCY BETWEEN 0.1 HZ AND 0.96 HZ:
   
  if ((frequencia_desejada >= 0.1)&&(frequencia_desejada < 0.96))
  {
    TCCR4E = 0b10000000;
    TCCR4A = 0b00000000; // Disabling PWM mode for pins OC4A, OC4A inverted, OC4B and OC4B inverted.
    TCCR4C = 0b00000000; // Disabling PWM mode for OC4D and OC4D inverted pins.
    TCCR4E = 0b00000000;
    digitalWrite(pino_OCR4D,HIGH);
    digitalWrite(pino_OCR4D_invertido,LOW);
    if ((largura_do_pulso_desejada*1000) < 1) // If the desired pulse_width is less than 1 ms, it is necessary to use the delayMicroseconds () function.
    {
      delayMicroseconds(largura_do_pulso_desejada*1000000);
    }
    else
    {
      delay(largura_do_pulso_desejada*1000);
    }
    digitalWrite(pino_OCR4D,LOW);
    digitalWrite(pino_OCR4D_invertido,HIGH);
     if ((largura_do_pulso_desejada*1000) < 1) // If the desired pulse_width is less than 1 ms, it is necessary to use the delayMicroseconds () function.
    {
      delayMicroseconds(largura_do_pulso_desejada*1000000);
    }
    else
    {
      delay(largura_do_pulso_desejada*1000);
    }
    digitalWrite(pino_OCR4D_invertido,LOW);
     if ((largura_do_pulso_desejada*1000) < 1)
    {
      delayMicroseconds((0.002-(2*largura_do_pulso_desejada))*1000000); // Accuracy improvement
      delay(((1.0/frequencia_desejada)-0.002)*1000);
    }
    else
    {
       delay(((1.0/frequencia_desejada)-(2*largura_do_pulso_desejada))*1000);
    }
  }
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

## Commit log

2021-06-30 3D Printing
    [Box.skp, Cover.skp, Print_Box.stl, Print_Cover.stl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]
2021-06-30 Arduino Code
2021-06-30 Arduino Library
